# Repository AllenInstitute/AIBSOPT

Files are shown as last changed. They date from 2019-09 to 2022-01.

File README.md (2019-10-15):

Optical projection tomography microscope for isotropic imaging of intact, cleared mouse brains.  Designed specifically for imaging probe tracks in mouse brains following Neuropixels recordings. 

Instrument described is very low cost (~$6k US), straightforward to assemble out of mostly commercially-available parts, and with little need for maintenance or alignment.

Images acquired by this instrument can be reconstructed using free NRecon software (SkyScan via Bruker) and aligned to Allen Institute for Brain Science Common Coordinate Framework. Detecting probe tracks in these images allows registration of multiple experiments into a common spatial framework for comparing results across experiments. 

Repository contents:
- 412792_fluorSubset.gif - stack of reconstructed images from portion of mouse brain showing multiple Neuropixels tracks
- .\InstrumentBuild : 
    - Parts list
    - .\CAD : CAD design for instrument
    - .\EAGLE : Schematic for motor control shield.
    
- .\Software : 
    - .\InstrumentSoftware :  
      - .\Arduino\diyOPT : Sketch for motor driver board
      - .\MicroManager : Config file and acquisition script for data acquisition
    - .\DataProcessing : 
        - Python code to generate files + folders for NRecon reconstructions
        - Python utilities to aid in alignment using images of a test object on instrument
    - .\Analysis : Code for post-reconstruction volume registration and probe tracing 
- .\Protocols : 
  - Standard operating protocol for sample mounting, instrument operation, and reconstruction with NRecon.

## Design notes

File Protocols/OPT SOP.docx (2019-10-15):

OPT SOP

Technical Authors & Contributors

Department | Name
Imaging | Rusty Nicovich, Mike Taormina , Nhan-Kiet Ngo
Structured Science

Date of SOP Creation (Version 1.0): 7/1/2019

Periodic Review

[ ] Biannual [ ] Annual [ ] Biennial [x] None Last Review: 10/14/2019

Departmental Sign-Off

Department | Approval Required | SOP Reviewed | Name
Imaging | [ ] | [ ] | Rusty Nicovich
Engineering | [ ] | [ ]
Health and Safety | [ ] | [ ]
Scientific Lead | [ ] | [ ]

1.0 Scope: This protocol describes the imaging and image processing of OPT.
2.0 Materials:
  2.1. Specially cleared mouse brain specimens.
  2.2. Loctite 404 superglue.
  2.3. Stainless steel circular mounting disks.
  2.4. Kimwipes.
  2.5. Tweezers.
  2.6. Solid waste bag.
  2.7. Dibenzyl ether.
  2.8. Razor blade.
  2.9. 100% ethanol.
3.0 Equipment:
  3.1. OPT imaging platform.
  3.2. Processing computer.
  3.3. External hard drive.
4.0 Safety:
  4.1. Nitrile Gloves.
  4.2. Lab coat.
5.0 Output: Fully imaged whole mouse brain in white and fluorescent lights.
6.0 Reference Documents:
  6.1. None.
7.0 Data Acquisition:
  7.1. Press the power button on the OPT machine.
  7.2. Press the On/Off button.
  7.3. Select Recall 2 to enable 18.0 V, < 1 A output on channel 2.
  7.4. Open Micro-Manager 2.0 on the computer and select the default options. Click Ok. See 7.4.1.

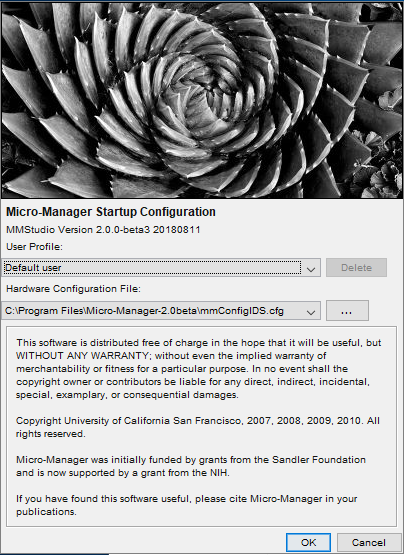
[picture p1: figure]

  7.5. Go to Tools → Script Panel → optacp.bsh.
    7.5.1. Create a storage folder in the following directory: D:\diyOPT\ and name the new folder using the following convention: xxxxyyzz where xxxx is the 4-digit year, yy is the 2-digit month, and zz is the 2-digit day.
    7.5.2. In optacp.bsh, baseFile = "" is the 6-digit specimen ID. Rename rootDirName = "D:/diyOPT/xxxxyyzz" to match the new folder just created. Then click "save". See 7.5.3 for example.

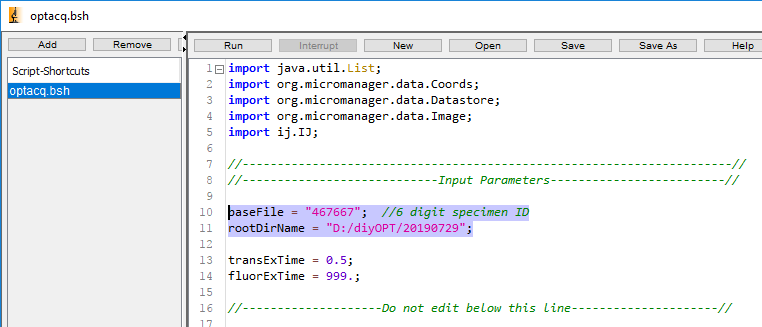
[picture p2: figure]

  7.6. Select a specimen to be imaged.
  7.7. Use a pair of tweezers to take the specimen out of its storage vial.
  7.8. Gently dab dry the specimen with Kimwipes.
  7.9. One small drop of Loctite 404 in the center of the mounting disk.
  7.10. Glue the cerebellum end of the specimen on to the disk. Wait at least one minute before using the tweezers to gently tap the specimen to make sure it's well glued.
  7.11. Mount the disk to the OPT imaging assembly.
  7.12. Center the disk and brain on the assembly. Tip: spin specimen with motor advance button on controller. At same time, use rounded object such as screwdriver handle to gently push disk to center brain on motor axis.
  7.13. Fill the imaging chamber with dibenzyl ether.
  7.14. Place the filled imaging chamber in the imaging area.
  7.15. Gently mount the imaging assembly into four post holders surrounding the filled imaging chamber. Make sure the amount of dibenzyl ether in chamber covers at least 1/3 of the specimen disk height but not completely submerge the disk. If there's any trapped air bubbles under the specimen disk, spin the mounting disk several times to get rid of them.
  7.16. Micro Manager control panel.

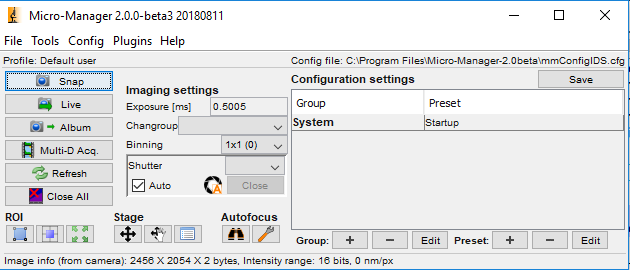
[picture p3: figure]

    7.16.2. In the Micro Manager control panel, click on Live. Turn the white light slide switch from TRIG to CW mode. White LED should now illuminate sample. In live view, determine the following:
      7.16.2.1. To determine the accurate exposure, adjust the light intensity (using LED controller knob) or exposure time (in MicroManager window) so that saturated hot spots just disappear and you have an even illuminating background without saturation. Using the limit-highlighting colormap is helpful here. See example of correct illumination in 7.15.2.2.

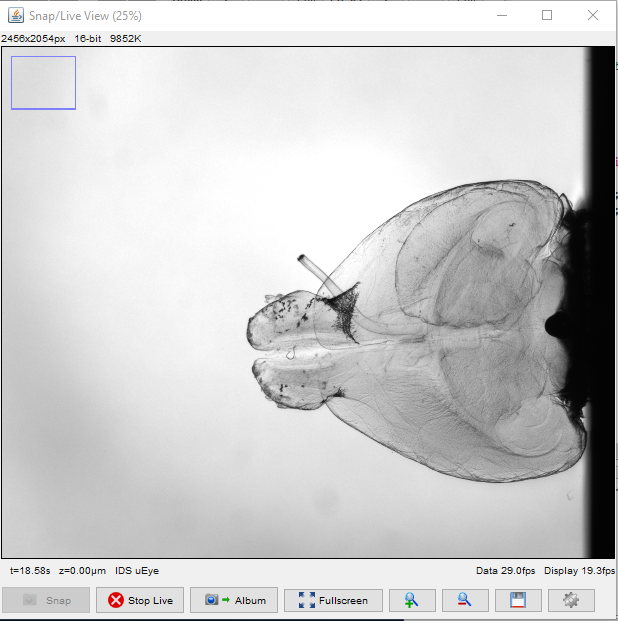
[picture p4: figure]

      7.16.2.3. The brain is well within the imaging area.
      7.16.2.4. Specimen is in focus.
      7.16.2.5. Use the stage micrometers to make any necessary adjustments to position and focus.
    7.16.3. Turn off live view (click ‘Stop Live’ in Micro Manager) and set white light controller to ‘TRIG’ position.
  7.17. Cover up the entire imaging platform with its box.
  7.18. After entering the 6-digit specimen ID in the optacq.bsh, click "Save" then "Run" in the script panel.
  7.19. The imaging process takes about six minutes to complete.
  7.20. Gently remove the imaging assembly from posts.
  7.21. Remove the mounting disk from the mechanism.
  7.22. Use razor blade safely and gently remove the brain from the disk.
  7.23. Use tweezers to place the specimen back into its original storage vial.
  7.24. Anything that comes directly in contact with dibenzyl ether needs to be throroughly cleaned by 100% ethanol. Solid waste goes into its storage bag.
  7.25. Use razor blade to remove any glue residue on the mounting disk.
  7.26. Store the specimens appropriately.
  7.27. Transfer the newly collected data to the processing station via the external hard drive.
8.0 Data Processing.
  8.1. On the processing computer, in D:\Data\diyOPT\ create a folder with exact same name as the data folder want to transfer over. This is the data storage folder.
  8.2. Open Spyder and script stackToPlanes.py. Set script variables to:
    8.2.1. inputFolder: Directory path of data folder from the external hard drive.
    8.2.2. outputFolder: Directory path of data folder created in 8.1. See example in 8.2.3

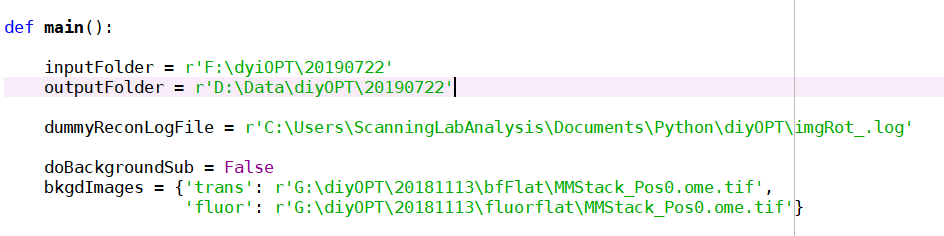
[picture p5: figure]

    8.2.4. Run stackToPlanes.py script in Python. Images and folders should be created in destination outputFolder designated in steps 8.1 and 8.2.3.
  8.3. Open Nrecon, then open specimen folder to be processed.
  8.4. Open the translucent (trans) folder first. Select the first image.
  8.5. Start tab:
    8.5.1. Position the green horizontal line at the specimen's widest section.
    8.5.2. Position the top horizontal line to be above speciemen's highest point.
    8.5.3. The value for bottom horizontal line is the amount necessary to exclude the black bar. See 8.5.3.1 for example:

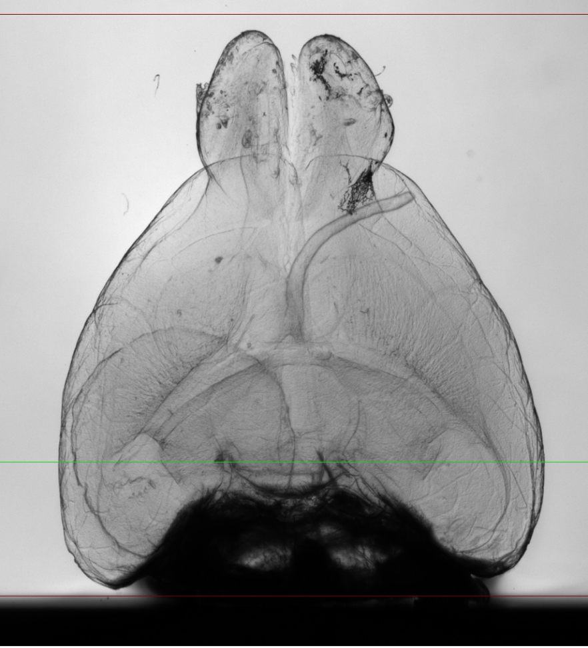
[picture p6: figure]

Black bar

    8.5.4. Record the values for Top and Bottom of range.
    8.5.5. Example:

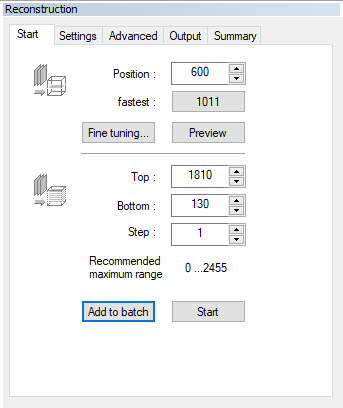
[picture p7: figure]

  8.6. Settings tab.
    8.6.1. Set Smoothing value to 3.
    8.6.2. Set Misalignment compensation value. This value is usually but not always, between -25 and -35. If the range is out side of -25 and -35, change the value until images align directly on top of each other. There should be no double images.
    8.6.3. Example:

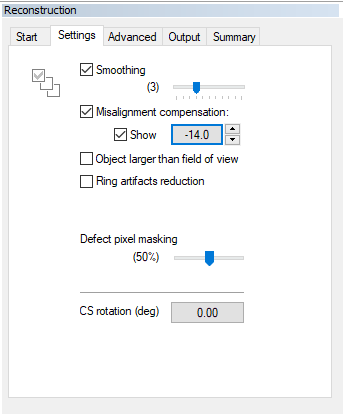
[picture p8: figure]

  8.7. Output tab.
    8.7.1. Uncheck Scales ON box.
    8.7.2. Destination: Browse and open the recon folder in the trans folder.
    8.7.3. File format: TIF(16).
    8.7.4. Example:

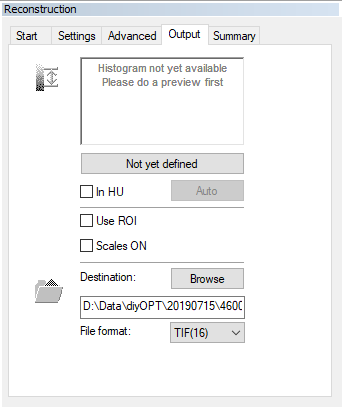
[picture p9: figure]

  8.8. Back to Start tab → Fine tuning → Number of trials = 10 trials → Start → Ok.
    8.8.1. Example:

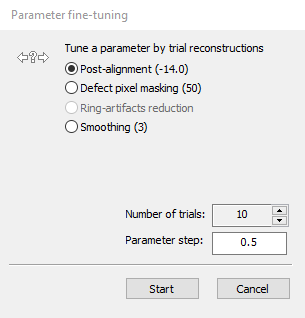
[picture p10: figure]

  8.9. After the trials are completed, in the Output tab, select the right vertical line and set all the way to the right of the histogram. Select the left vertical line and place it to the left of the base of the peak.
    8.9.1. Example:

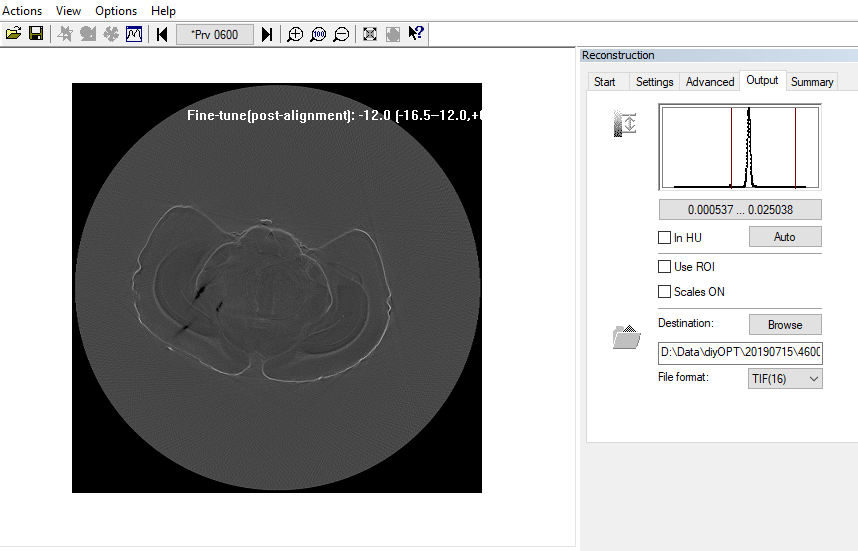
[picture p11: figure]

  8.10. Click on either the foward or backward arrow to determine the best-aligned image.
    8.10.1. Perfect alignment: top, bottom, left, and right all align with each other.

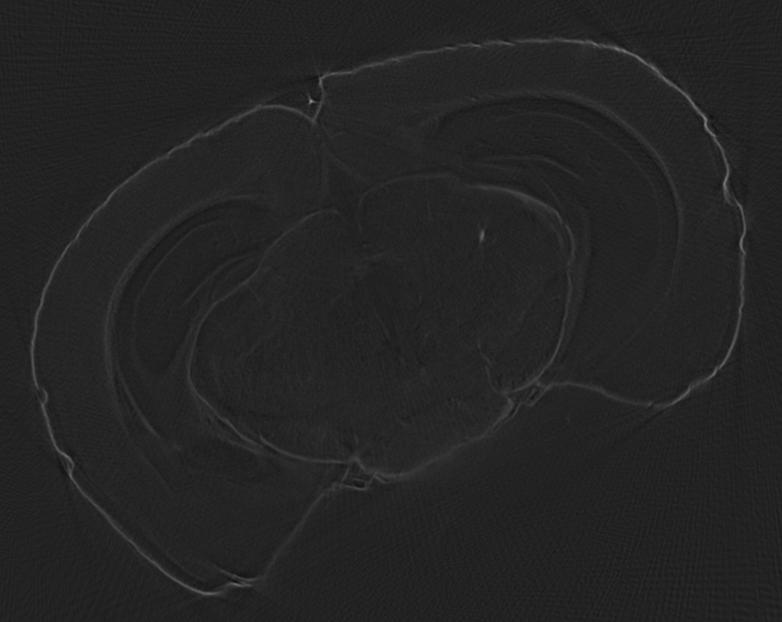
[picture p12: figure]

    8.10.2. Bad alignment: double image.

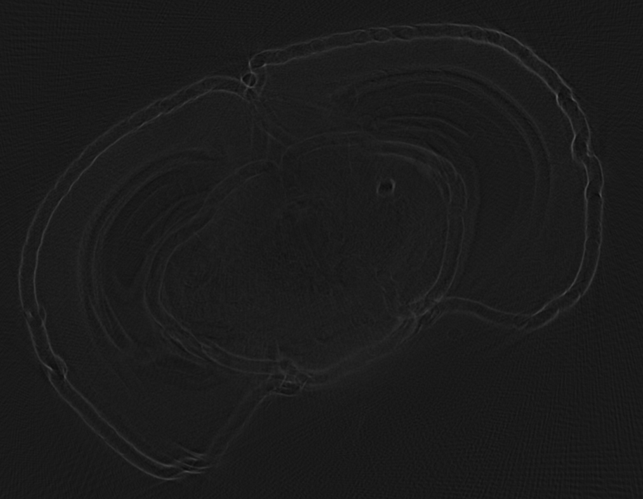
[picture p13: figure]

    8.10.3. Very poor alignment: no two parts can perfectly align with each other.

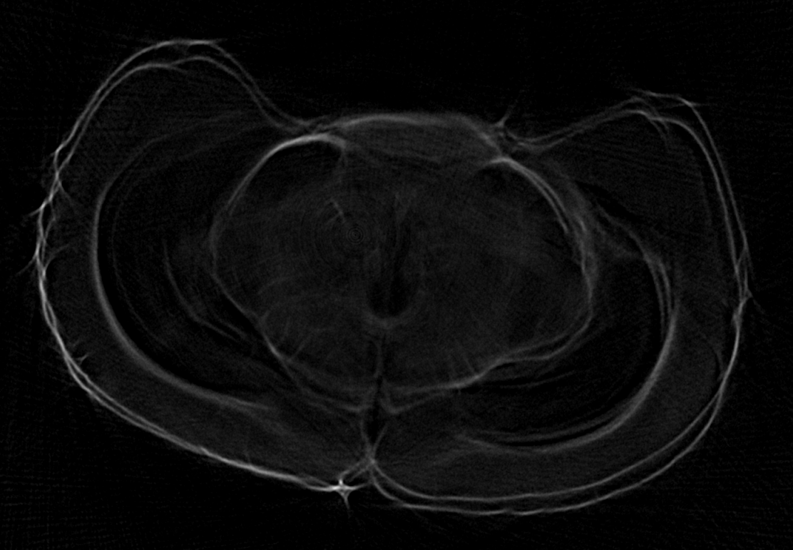
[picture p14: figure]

  8.11. Start tab → Add to batch.
  8.12. Open the fluorescent (fluor) folder of the same specimen. Select the first image, and repeat steps 8.5 – 8.9. For steps 8.5.1 – 8.5.4, enter the values for Top, Bottom, and Misalignment compensation you got from the transmitted channel. Make sure the destination is the recon folder inside the fluor folder.
  8.13. After completing all above steps for all specimens needed to be processed, go through the pending list to make sure all are 16-bit TIF.
  8.14. Start batch and let the processing runs overnight.
  8.15. Upon completion the next day, transfer data to the project's directory over the network.
9.0 Takedown:
  9.1. Clean work area. All items exposed to dibenzyl ether must be cleaned thoroughly by 100% ethanol.
  9.2. Store solid waste in its storage bag.
  9.3. Return the dibenzyl ether tub to the hood. Place a cover on it.
10.0 Precautionary: Dibenzyl ether is mildly toxic and corrosive. It's both storage and imaging medium. Wear PPE and exercise appropriate precautions.

Page 2 of 12 OPT SOP

Page 2 of 5 OPT SOP

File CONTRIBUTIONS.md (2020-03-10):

Allen Institute Contribution Agreement
This document describes the terms under which you may make “Contributions” — which may include without limitation, software additions, revisions, bug fixes, configuration changes, documentation, or any other materials — to any of the projects owned or managed by the Allen Institute. If you have questions about these terms, please contact us at terms@alleninstitute.org.  
You certify that:
•	Your Contributions are either:
1.	Created in whole or in part by you and you have the right to submit them under the designated license (described below); or
2.	Based upon previous work that, to the best of your knowledge, is covered under an appropriate open source license and you have the right under that license to submit that work with modifications, whether created in whole or in part by you, under the designated license; or
3.	Provided directly to you by some other person who certified (1) or (2) and you have not modified them.
•	You are granting your Contributions to the Allen Institute under the terms of the 2-Clause BSD license (the “designated license”).
•	You understand and agree that the Allen Institute projects and your Contributions are public and that a record of the Contributions (including all metadata and personal information you submit with them) is maintained indefinitely and may be redistributed consistent with the Allen Institute’s mission and the 2-Clause BSD license.

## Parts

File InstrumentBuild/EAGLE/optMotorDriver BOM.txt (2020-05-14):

Bill of Materials:

Motor Driver

Qty 1	-	PCB - https://oshpark.com/shared_projects/akx3myRT
Qty 1	-	BigEasyDriverBoard; Sparkfun ROB-12859
Qty 48	-	Male header strip; Adafruit 392 or equivalent
Qty 1	-	Wurth Electronik 62400821722 - 2 x 4 pin connector
Qty 8	-	Adafruit 1 x 2 @ 3.5 mm screw terminal 
Qty 7	-	10kΩ resistors, 1206 package
Qty 1	-	5.2mm SMD tactile switch
Qty 1	-	2.1mm x 5.5mm THM DC jack with internal switch. Digikey part #PJ-102A, 4UCON part #05537   

Button board

Qty 1	-	PCB	-	https://oshpark.com/shared_projects/rrk3NWli
Qty 2	-	Sparkfun COM-09190 - 12 mm pushbutton switch
Qty 5	-	Nidek Copal Electronics ATE1E-2M3-10-Z - toggle switch
Qty 1	-	Wurth Electronik 62400821722 - 2 x 4 pin connector

Connector cable

Qty 2	-	Wurth Electronik 624008213322 - 2 x 4 pin terminal housing
Qty 16	-	Molex 0008700058 crimp socket, 22-28 AWG
Qty 1	-	8 connector, 26 AWG cable, 1m; Tensility International Corp 30-01319

------------------------------------------------------------------------------------

Build Notes:

Stepper motor mounts to A and B coil ports. Connect light sources to 'ChanX' output terminal block.  
Thorlabs LED T cubes connect through BNC pigtail cable. 
Connecting camera to trigger terminal is optional.  
Power through wall wart supply with 5.5 mm x 2.1 mm connector, 12v, 0.5 A output.

Button board lets you switch on/off channels, move motor outside the enclosure.

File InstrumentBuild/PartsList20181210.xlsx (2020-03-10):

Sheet: DemoSystem
Sub-asssembly | Component | Vendor | Part Number | Qty | Price per | Total price | Notes
Imaging | Imaging lens | Edmund Optics | 62-932 | 1 | $1495.00 | $1495.00
 | Thread adapter | Edmund Optics | 59-450 | 1 | $25.00 | $25.00
 | Emission filter | Edmund Optics | 64-635 | 1 | $195.00 | $195.00 | 50 mm; 575 LP
 | Imaging lens mount | Edmund Optics | 63-442 | 1 | $295.00 | $295.00
 | Mount risers | Thorlabs | RS4M | 3 | $7.67 | $23.01 | Under lens mount
 | Filter holder | Edmund Optics | 83-340 | 1 | $50.00 | $50.00
 | Camera | 1st Vision | UI-3280CP | 1 | $1030.00 | $1030.00 | 2/3" format; 3.45 µm pixels
Fluor LED | Excitation LED | Thorlabs | M530L3 | 1 | $223.00 | $223.00
 | Collimation lens | Thorlabs | ACL2520U-DG6-A | 1 | $29.94 | $29.94
 | Excitation filter | Chroma | ET535/70m-2P | 1 | $375.00 | $375.00
 | LED driver | Thorlabs | LEDD1B | 1 | $314.13 | $314.13
 | LED mount | Thorlabs | SM1RC | 1 | $24.37 | $24.37
 | Power supply | Thorlabs | KPS101 (https://www.thorlabs.com/thorproduct.cfm?partnumber=KPS101) | 1 | $34.33 | $34.33
 | Lens tube | Thorlabs | SM1L05 | 2 | $12.59 | $25.18 | One upstream of adjustable tube; one w/ filter
 | Pedistal post | Thorlabs | RS1P | 1 | $23.64 | $23.64
 | Post clamp | Thorlabs | CF038-P5 | 0.2 | $40.19 | $8.04
 | Pedistal spacer | Thorlabs | RS3M | 1 | $7.67 | $7.67
 | Lens tube, adjustable | Thorlabs | SM1V05 | 1 | $30.25 | $30.25
Trans LED | Transmission LED | Thorlabs | MNWHL4 | 1 | $154.50 | $154.50
 | Lens tube, 0.3" | Thorlabs | SM1L03 | 1 | $12.16 | $12.16
 | LED collimator | Thorlabs | SM2F32-A | 1 | $277.36 | $277.36
 | Diffuser | Thorlabs | DG20-600 | 1 | $18.07 | $18.07
 | LED mount | Thorlabs | SM1RC | 1 | $24.37 | $24.37
 | Post clamp | Thorlabs | CF038-P5 | 0.2 | $40.19 | $8.04
 | Pedistal post | Thorlabs | RS1P | 1 | $23.64 | $23.64
 | Pedistal spacer | Thorlabs | RS3M | 1 | $7.67 | $7.67
 | LED driver | Thorlabs | LEDD1B | 1 | $314.13 | $314.13
 | Power Supply | Thorlabs | KPS101 (https://www.thorlabs.com/thorproduct.cfm?partnumber=KPS101) | 1 | $34.33 | $34.33
XY Stage assembly | XY Stage | Thorlabs | XYT1 | 1 | $552.62 | $552.62
 | 1/2" posts | Thorlabs | TR2 | 4 | $5.19 | $20.76 | 2" long
 | Post holders | Thorlabs | PH2 | 4 | $7.70 | $30.80 | 2" long
 | Post bases | Thorlabs | BE1 | 4 | $9.77 | $39.08
 | Post clamps | Thorlabs | CF038-P5 | 1.6 | $40.19 | $64.30 | May need CF125; 4 for stage and 4 for breadboard
 | Post collars | McMaster | 6157K14 | 4 | $2.94 | $11.76
 | Breadboard | Thorlabs | MB624 | 1 | $157.59 | $157.59
 | Breadboard feet | Thorlabs | RS1P | 4 | $23.64 | $94.56
Motor and sample mount | Rotating bearing | McMaster | 6383K23 | 1 | $5.52 | $5.52
 | Retaining rings | Thorlabs | SM1RR | 2 | $4.50 | $9.00
 | Shaft | -- | -- | 1 |  |  | Made in-house
 | Magnetic chuck | Thorlabs | BE1R | 1 | $17.23 | $17.23
 | Brain pucks | -- | -- | 1 |  |  | Made in-house; Make additional for throughput
 | Motor | -- | -- | 1 |  |  | 0.9 degree; NEMA 17
 | Motor mount | -- | -- | 1 |  |  | Made in-house
 | Motor lift mounts | Thorlabs | RS1P | 4 | $23.64 | $94.56
 | Motor lift mount clamps | Thorlabs | CF038-P5 | 0.8 | $40.19 | $32.15
Control electronics | Control board | SparkFun | DEV-11021 | 1 | $22.95 | $22.95
 | Motor driver | SparkFun | ROB-12859 | 1 | $19.95 | $19.95 | On in-house shield
 | USB-A to USB-B cable | Amazon | B00NH11KIK | 1 | $5.10 | $5.10 | 6' long
 | BNC pigtail cable | -- | -- | 2 |  |  | Made in-house
 | Power supply | -- | -- | 1 |  |  | Must supply 18V @ 1 A; 5.5 mm x 2.1 mm connector with optMotorDriver
 | Board mount | -- | -- | 1 |  |  | In-house design; 3D printed
 | Motor driver Arduino shield | -- | -- | 1 |  |  | In-house design; See ./AIBSopt/EAGLE/
PC | Control PC | -- | -- | 1 |  |  | 1 x USB 2.0+; 1 x USB 3.0; 3+ TB HDD; Win 10 OS
 |  |  |  | Total | $6260.76

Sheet: LaserLaunch
Sub-asssembly | Component | Vendor | Part Number | Qty | Price per | Total price | Notes

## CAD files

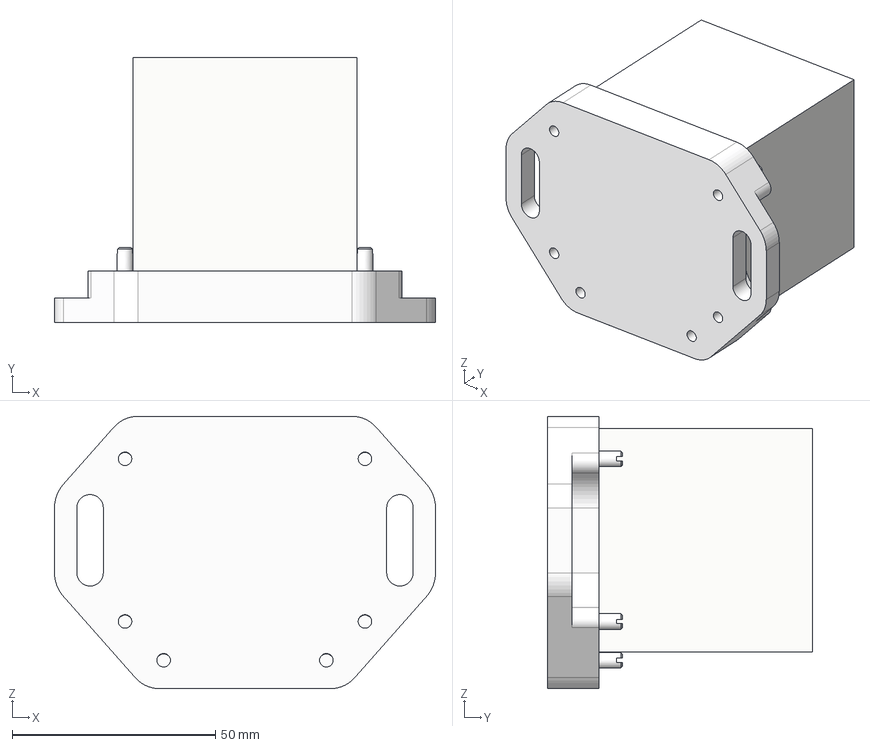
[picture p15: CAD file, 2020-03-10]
InstrumentBuild/CAD/toMachine/CuvetteStandAssembly.step
93.7 x 65.2 x 67.0 mm
50mmCuvette
McMaster 97493a114 x 6

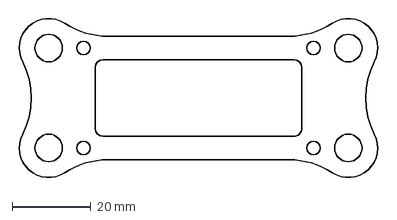
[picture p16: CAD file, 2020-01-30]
InstrumentBuild/CAD/DriverBoard/OPTButtonBoardTableMount.dxf
92.7 x 41.7 mm

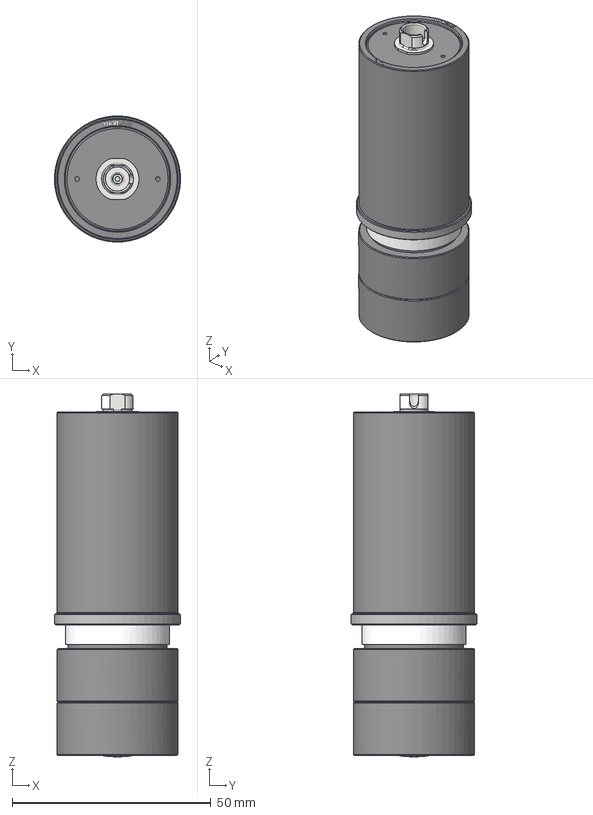
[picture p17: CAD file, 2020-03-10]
InstrumentBuild/CAD/LaserLaunch/hexLaserCoupler.step
31.7 x 31.7 x 91.3 mm
94355A140 x 6
HexLightPipeToSM1Adapter
SM1L05-Solidworks
SM1V05-Solidworks v1
SM1RR x 2
AC254-035-A-Solidworks
SM1FC-Solidworks
step_65830
SM1M20-Solidworks v1

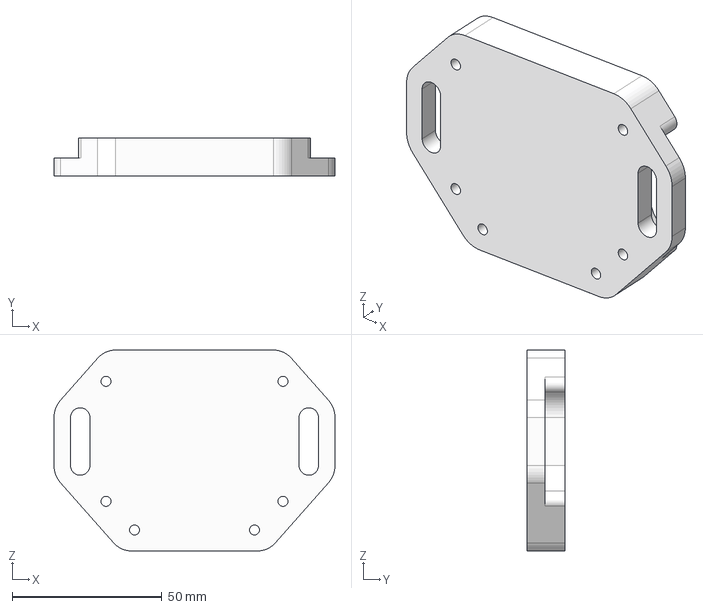
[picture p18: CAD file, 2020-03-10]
InstrumentBuild/CAD/toMachine/OPTCuvetteBase.step
93.7 x 12.7 x 67.0 mm

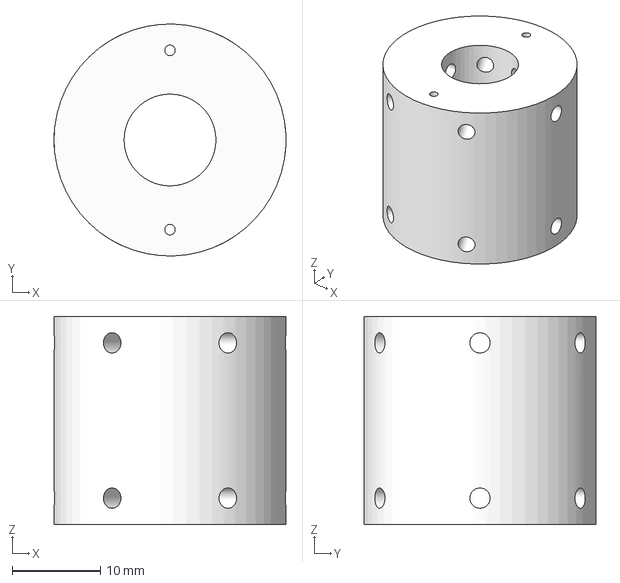
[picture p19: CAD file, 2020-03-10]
InstrumentBuild/CAD/toMachine/HexLightPipeToSM1Adapter.step
26.3 x 26.3 x 23.6 mm

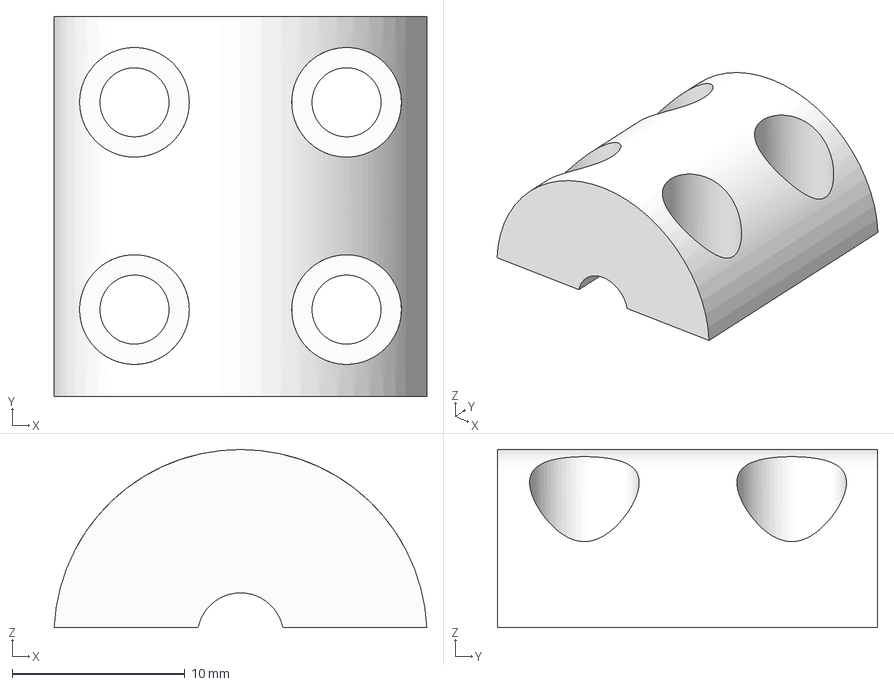
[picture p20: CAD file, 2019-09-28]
InstrumentBuild/CAD/toMachine/BearingShaftClamp.step
21.6 x 22.0 x 10.3 mm

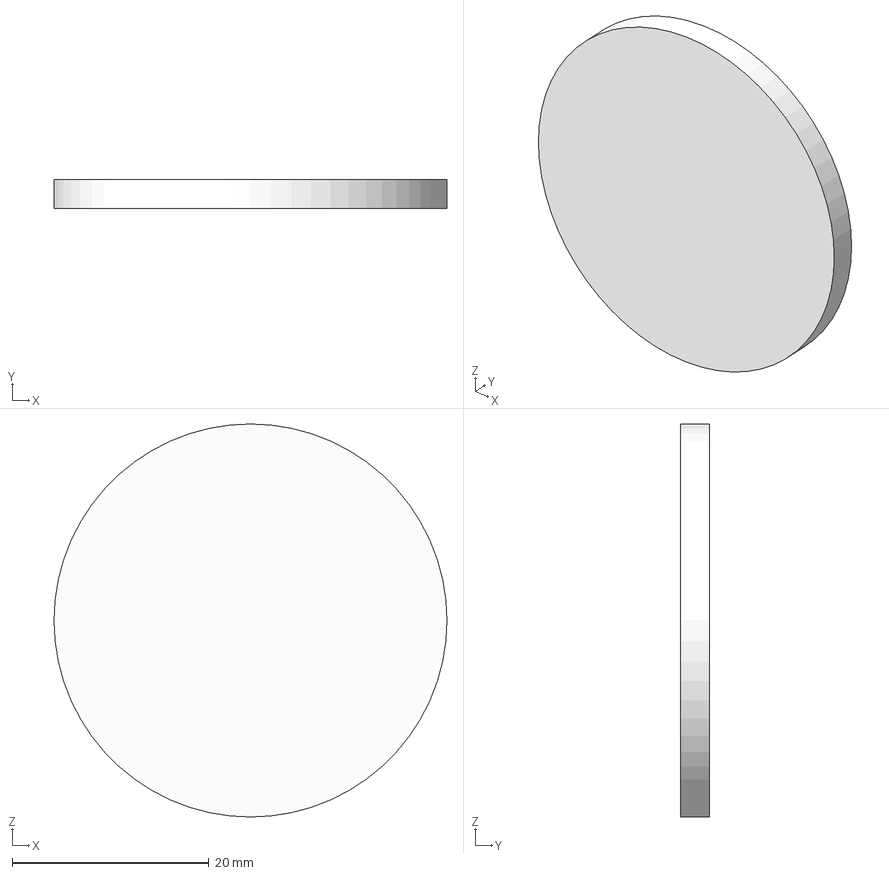
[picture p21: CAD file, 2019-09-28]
InstrumentBuild/CAD/toMachine/sampleHolderPuck.step
40.0 x 3.00 x 40.0 mm

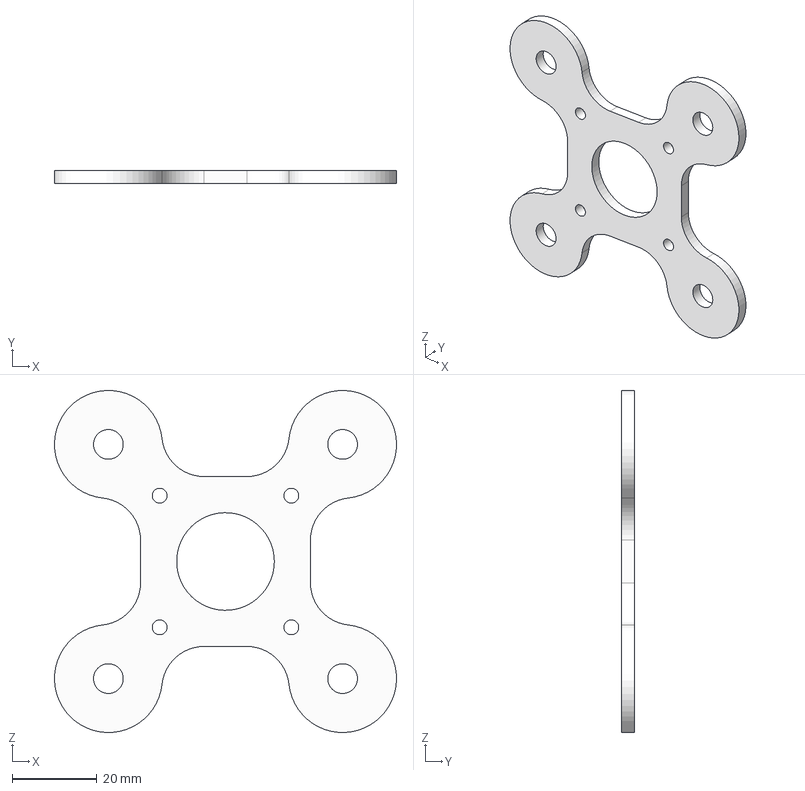
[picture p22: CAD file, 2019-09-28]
InstrumentBuild/CAD/toMachine/Nema17OPTmotorMountv2 v2.step
80.5 x 3.18 x 80.5 mm

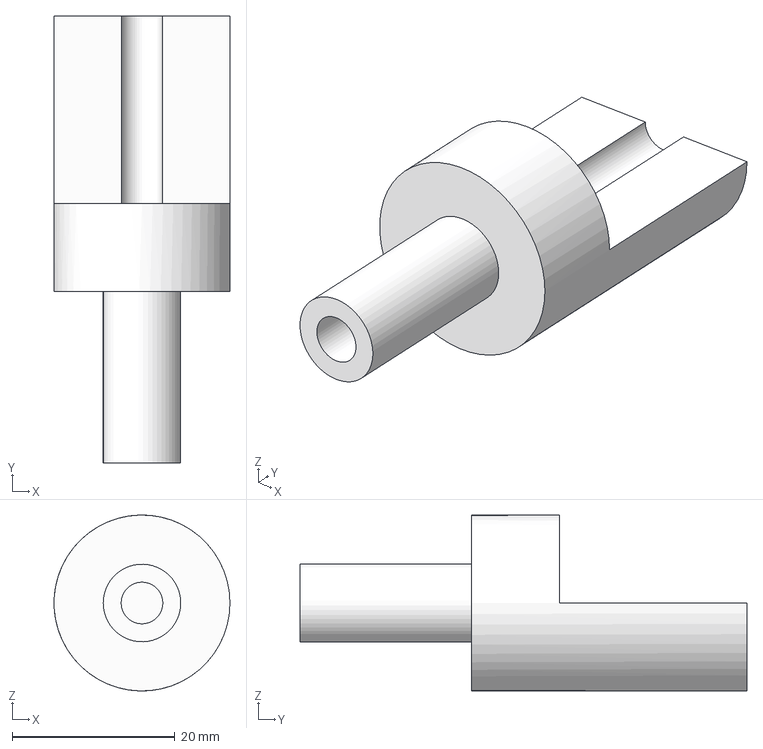
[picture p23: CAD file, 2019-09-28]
InstrumentBuild/CAD/toMachine/BearingShaft.step
21.6 x 54.9 x 21.6 mm

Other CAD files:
InstrumentBuild/CAD/toMachine/HexLightPipeToSM1Adapter.stl

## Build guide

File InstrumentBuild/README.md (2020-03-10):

Components and assembly for AIBSOPT

# CAD
	Includes STEP file of instrument assembly with all physical components and instrument rendering.  
	
	.\CAD\toMachine includes individual STEP files and drawings of parts to machine:
		- Extended motor shaft (BearingShaft.step, BearingShaftClamp.step, diyOPTShaftExplode Drawing v0.pdf). Make 1 assembly from aluminum. 
		- Motor mount (Nema17OPTmotorMountv2 v2.step and .pdf). Make 1 from aluminum. 
		- Sample holder puck (sampleHolderPuck.pdf and .step).  Make 1-4 from *magnetic* stainless steel.
		- Specimen chamber (specimenChamberBuildNotes.txt):
			DIY - slideSpecimenChamber drawing v1.pdf
			----OR----
			Purchase Hellma 50 mm large cuvette (Sigma-Aldrich part Z805750), machine OPTCuvetteBase.step, assemble CuvetteStandAssembly.step

	.\CAD\DriverBoard
		- Files to laser cut mount for optMotorButtonBoard to Imperial optical table.  Cut from acrylic and use standard PCB stand-offs to mount PCB.
		
	.\CAD\laserLaunch
		- Assemblies and build details on adding laser illumination to OPT.  Includes laser combiner + launch w/ speckle reducer and fiber coupling, enclosure, and laser illuminator.

# PCB Files

	.\EAGLE : Schematic for Arduino motor shield and remote button board for instrument control.
		- optMotorDriver BOM.txt includes parts required for assembly and links to order PCB
		- Can upload .brd files to favorite PCB fab service to order
		- Mount to optical table with .\CAD\DriverBoard part

# Notes on assembly and alignment:

Final resolution of instrument is primarily dependent on alignment of all images in the rotation stack. The rotation axis *MUST* be aligned to camera optical axis, with no roll or pitch.  Yaw is actually well-tolerated.  Roll (camera rotating around optical axis/rotational axis tilted left or right) and pitch (aka nod, rotation axis tilted towards or away from camera) manifest as misalignment in the collected image stack and blur or double-image artifacts in the reconstructions.  

Steps for aligning the roll and pitch axes follow those well-described in https://doi.org/10.1371/journal.pone.0073491.  An object, such as a small ball bearing or tip of a hypodermic needle mounted on the sample holder using glue and/or magnets, provides a good fiducial marker.  This item or a feature on it should be able to be localized in images to sub-pixel precision.  Tracking this feature through the stack should produce a straight line parallel to one axis of the camera.  Any tilt is evidence of roll; elliptical character evidence of pitch.  The .\Software\DataProcessing\assessTestObject.py script is helpful in this step.

Adjustments can be made through small movements of the XY stage and motor.  This assembly should rest equally on all four of the shaft collars on the 1/2" mounting posts.  Typically the screws in the post holders are left open so that the posts freely drop to the proper position.  Shims made from shim stock or a cleaned and dissected soda can make small adjustments to the stage tip or tilt for testing alignment.  If a good position is found, this can be set in place by tightening the post holder screws with the shims in place, removing the shims, then lowering the shaft collars hard against the post holders before tightening the collar screws.  Then when the stage is lifted out and returned, it should return to the same position defined by the shaft collars against the top of the post holders.

Additional care must be taken to have specimen remain within camera field of view while rotating and remain in focus.  Both are straightforward to deal with using the adjusters on the XY stage.  The depth of focus can be increased using the built-in aperture iris on the telecentric lens.  Best to have this be close to the full depth of the specimen without overly darkening the images.  In practice the lost sharpness in the images is negligable compared to the blur induced by mis-alignment.

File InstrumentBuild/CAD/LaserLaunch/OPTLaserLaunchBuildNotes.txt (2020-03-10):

Build notes for laser illumination on AIBS OPT.

Goal is to have a high-powered light source with narrow line widths for improved imaging performance over LED illumination.  Laser line widths make it easier to find appropriate optical filters for multi-colored imaging.  

For laser launch, requirement is for lasers in desired wavelengths combined into single multi-mode fiber with despeckler.  Implementation here is a simplified NicoLase 1200 design supporting two diode lasers (488 nm and 552 nm nominal wavelengths) with EvenField despeckler into Thorlabs square-core multimode fiber. Fiber choice is dictated by NA. The square-core Thorlabs fiber has an NA of 0.39; Thorlabs also sells a number of typical round-core fibers with same or higher NA for ~$50 less. Any should work but only the square-core fiber we had on hand was tested.   

Small footprint of the laser launch allows it to fit onto a 12" x 12" breadboard for easy deployment. Two lines is sufficient for desired experiments. Enclosure holds laser launch in compact box that is easy to fit on a shelf.  Drill some holes into top panel and you can use screws or zip ties to mount laser control remotes and motor driver board on exterior.  

Illuminator takes fiber output and generates homogeneous hexagon of light at the specimen plane. Using a fiber of lower NA could result in less even illumination out of the hexagonal light pipe. In that case a longer light pipe (eg the Edmund 50 mm 49-402 vs Edmund 25 mm 63-082 quoted here) may be adventageous. The illuminator assembly fits into lens tubes of similar dimension to Thorlabs LED, so swapping out illumination choices is straightforward.

Illuminator uses a single lens to project front hexagonal face of light pipe onto specimen. This means focusing and magnfication are coupled. For the #63-082 pipe, the front face is 4.0 mm across the flats.  The illuminator should sit near the OPT collection lens, but behind the front element of that component.  This is a minimum distance of ~170 mm from the specimen.  With a f = 35 mm lens, this would mean placing the lens (1 / 35 mm) = (1 / 170 mm) - (1 / x) ; x = 44 mm away from the light pipe output.  This yields a M = 170 / 44 = 3.8x magnification, for a spot 15.2 mm across the hexagonal flats.  If the distance was 190 mm, the spot would be 17.6 mm.  In most cases a smaller spot size is preferred to preserve illumination intensity over the specimen, so a shorter distance (or longer focal length lens) is preferred.
 
TTL outputs from laser head or remote can go directly into OPT Motor Board.  Home-made SMB pigtails were used on our implementation.  

Cost is mostly price of laser diodes ($~15k for models used here), with another $~3k in optics, filters, and machined parts to complete build. 

~~~~~~~~~~  Laser launch ~~~~~~~~~~  

Bill of Materials
To machine:
NicoLase 1200 heat sink block : https://github.com/PRNicovich/NicoLase/blob/master/Hardware/HeatSinkMount/NicoLase3200HeatSinkBlock.step
Evenfield motor block and arbor : https://github.com/AllenInstitute/EvenField/blob/master/Hardware/CAD/diffuserMotorAssembly.step

Thorlabs:
[NicoLase 1200]
MB1212
POLARIS-K1 x 2
RP05P x 2
PF10-01-P01 
CF125 x 2

[Evenfield coupler]
KB1C
PF10-01-P01 
CP02
SM1L10
S1TM09
C220TMD
CT1
CT102
SM05FC
ER6 x 2
ER3
CP02B
RS6M
RS3M
RS05P x 2
M102L05
CF125 x 2

Chroma:
ZT514rdc in 25 mm round, mounted 
nb - substitute with part appropriate for your lasers

Edmund
[Evenfield illuminator diffuser]
#47-989, mounting ring removed and center hole drilled.  See https://github.com/AllenInstitute/EvenField/blob/master/Hardware/CAD/diffuserMotorAssembly.step

Polou:
#3036, gear motor

Laser diodes:
Coherent OBIS 552 nm, 100 mW with remote
Vortran Stradus 488 nm, 150 mW with remote
Any NicoLase-compatible laser diode will work here if you want different wavelengths.

Optional:
Evenfield motor driver :
https://github.com/AllenInstitute/EvenField/tree/PCBAddition/Hardware/MotorDriverPCB

~~~~~~~~~~  Enclosure ~~~~~~~~~~ 

Assembly is in file ./AIBSOPT/InstrumentBuild/CAD/OPTLaserLaunch.step.

Bill of Materials
To machine:
Panels were made from 1/4" black foamcore (Thorlabs TB4).  
Top panel - 359 mm x 359 mm with 6.5 mm holes at 12.5 mm from corners, access slot for internal cables.
3 x Side panels - 324 mm x 150 mm with 12 mm x 15 mm knotchees in each corner. 
As per Side panel, but with 14 mm diameter holes for grommets for fiber, motor wires

80/20:
All 1" Series 10 T slot profile.  All taps 1/4"-20 and access holes 5.1 mm.
4 x 159 mm w/ end tapped, other end 2 x access holes at 12.7 mm
6 x 309 mm w/ both ends tapped
2 x 309 mm w/ both ends tapped, 2 x access holes on same face at 27 mm from either end
2 x 359 mm w/ 4 x access holes, 12.7 mm from both ends on both faces
Hardware:
20 x 3682 standard fastener
4 x 3313 roll-in T nut with set screw or similar
4 x 3382 slide-in T nut or similar

McMaster-Carr:
2 x 9307K131 grommets.  Split with knife to wrap around optical fiber.
4 x 9541K83 feet or similar

~~~~~~~~~~  Illuminator ~~~~~~~~~~ 

Bill of Materials:
To print/machine:
HexLightPipeToSM1Adapter - Print or machine from variety of materials - ./AIBSOPT/InstrumentBuild/CAD/toMachine/HexLightPipeToSM1Adapter.step or ./AIBSOPT/InstrumentBuild/CAD/toMachine/HexLightPipeToSM1Adapter.stl

Thorlabs:
SM1V05
SM1L05
2 x SM1RR
SM1FC
SM1M20
AC254-035-A (can substitute different focal length depending on application)

Edmund:
#63-082 light pipe

McMaster:
94355A217 or similar 4-40 set screws, 1/2" long recommended

~~~~~~~~~~  Emission filter ~~~~~~~~~~

Semrock FF01-512/630-50, mounted. Mount with existing adapter on front of collection lens.

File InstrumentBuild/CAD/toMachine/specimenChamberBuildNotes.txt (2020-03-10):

~~~~~~~~ DIY OPTION ~~~~~~~~ 

Specimen chamber for demo system built from 3 1/4" x 4" x 1.2 mm glass slides (Brain Research Laboratories part 3140).  These were cut to size w/ glass cutter and glued together with Dow Corning #732 clear silicone sealant.  That product from Dow has been robust to dibenzyl ether as immersion medium over months of use.  

Nominal dimensions of chamber are given in sliceSpecimenChamber drawing v1.pdf. As long as assembled chamber fits within space provided, can hold sufficient immersion medium to immerse specimen, and presents a flat face through transmission path to detection lens and to fluorescence excitation, dimensions can be altered significantly to suit.

~~~~~~~~ PURCHASE OPTION ~~~~~~~~ 

Commercial cuvette such as Hellma 50 mm large cell (Sigma-Aldrich Z805750) works well in this application.  Is easier to use and requires a smaller volume than the DIY cuvette above. Plus it doesn't have any chance of leaking!

On OPT, this cuvette sits on stand OPTCuvetteBase.step, machined from aluminum or other material impervious to immersion fluid.  This part has 6 places for 4 mm diameter locating pins (McMaster-Carr 97493A114), as shown in CuvetteStandAssembly.step.  In practice it is likely easier to use only 4, 2 to locate back edge of cuvette nearest to transmission path white LED, and 2 to locate one side of cuvette.  Then cuvette installation would involve pushing cuvette to be flush to these 4 pins.  Stand should be centered in light path and has some movement backwards + forwards towards collection lens to find best focus. Be sure to focus with target in immersion fluid in the cuvette!

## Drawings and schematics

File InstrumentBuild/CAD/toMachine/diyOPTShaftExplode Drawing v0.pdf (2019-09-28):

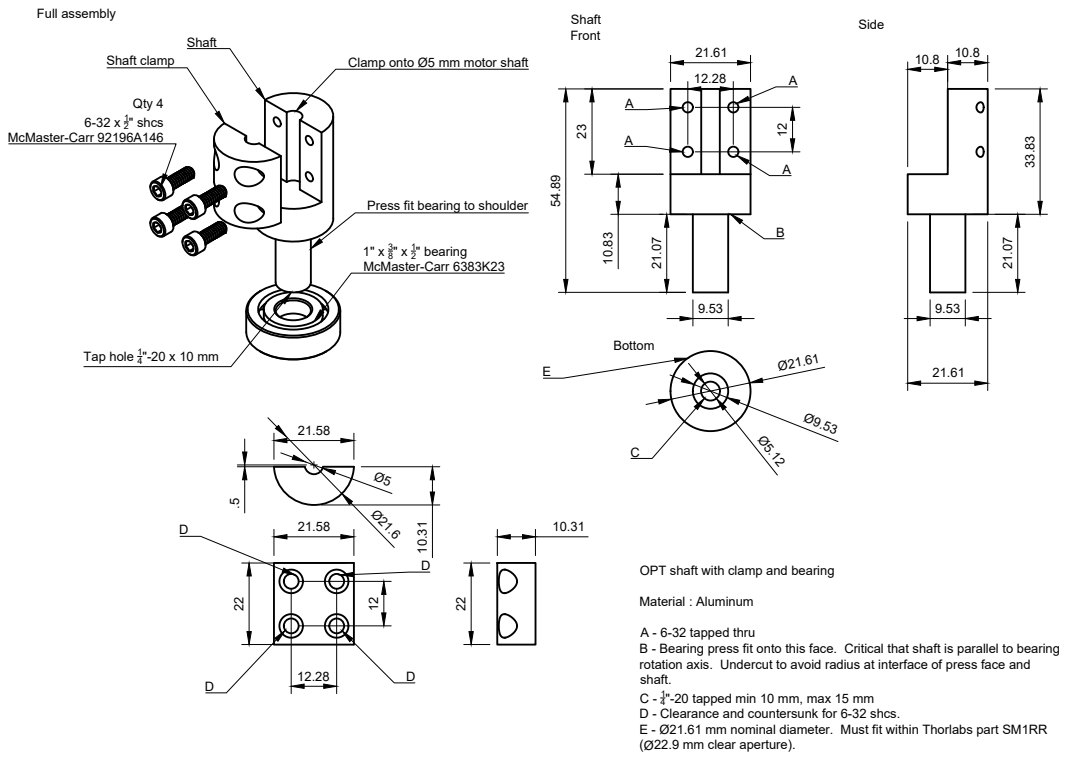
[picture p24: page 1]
Qty 4; 6-32 x 1 " shcs McMaster-Carr 92196A146; Shaft clamp; " x 1 " bearing McMaster-Carr 6383K23; Tap hole 1 "-20 x 10 mm; Material : Aluminum; Full assembly

Clamp onto Ø5 mm motor shaft

Press fit bearing to shoulder

OPT shaft with clamp and bearing

A - 6-32 tapped thru
B - Bearing press fit onto this face. Critical that shaft is parallel to bearing
rotation axis. Undercut to avoid radius at interface of press face and
shaft.
"-20 tapped min 10 mm, max 15 mm
D - Clearance and countersunk for 6-32 shcs.
E - Ø21.61 mm nominal diameter. Must fit within Thorlabs part SM1RR
(Ø22.9 mm clear aperture).

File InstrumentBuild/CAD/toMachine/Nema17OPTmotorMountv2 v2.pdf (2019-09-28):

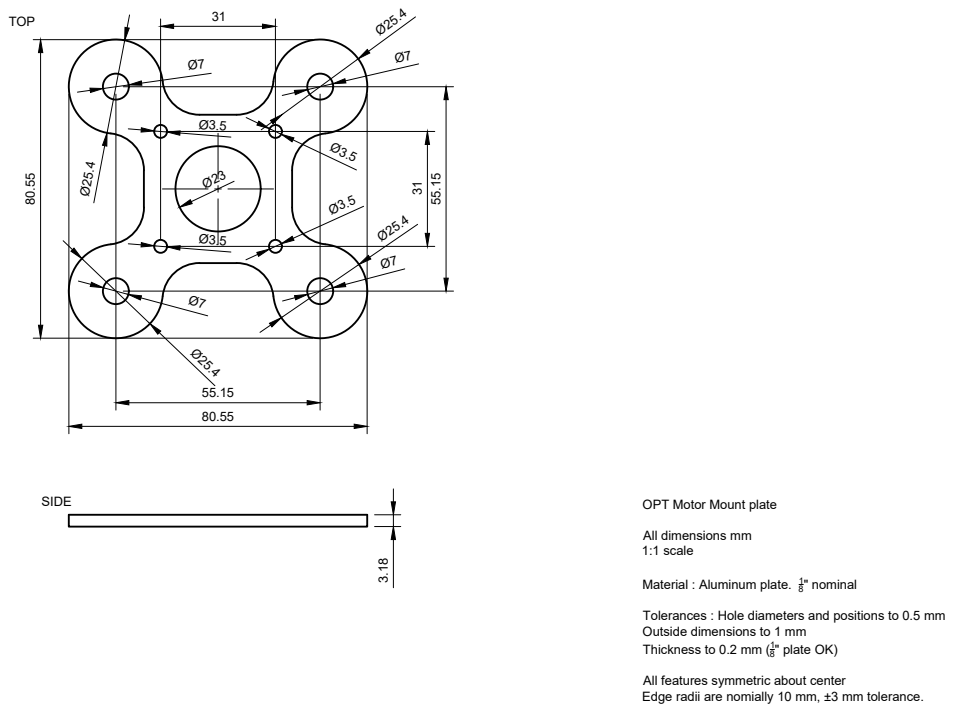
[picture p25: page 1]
" nominal; " plate OK)

OPT Motor Mount plate

All dimensions mm
1:1 scale

Material : Aluminum plate. 1

Tolerances : Hole diameters and positions to 0.5 mm
Outside dimensions to 1 mm
Thickness to 0.2 mm (1

All features symmetric about center
Edge radii are nomially 10 mm, ±3 mm tolerance.

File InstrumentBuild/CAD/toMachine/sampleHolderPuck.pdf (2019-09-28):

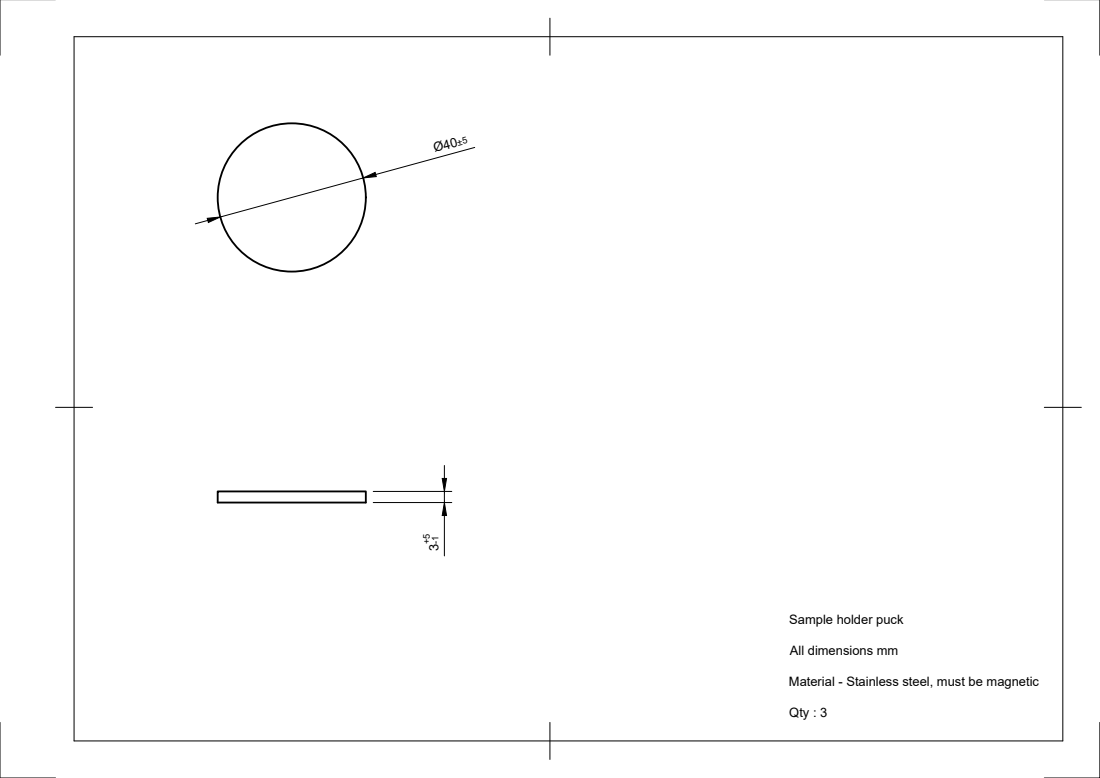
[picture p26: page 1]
Qty : 3

Sample holder puck

All dimensions mm

Material - Stainless steel, must be magnetic

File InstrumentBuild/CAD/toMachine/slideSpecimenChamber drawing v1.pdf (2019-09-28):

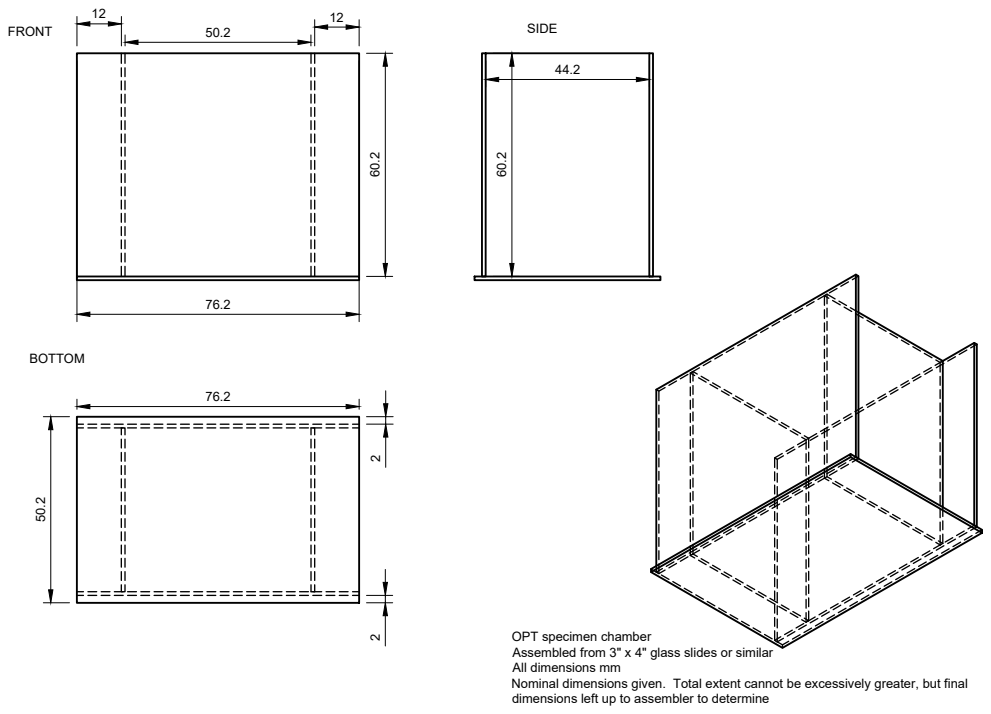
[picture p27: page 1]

OPT specimen chamber
Assembled from 3" x 4" glass slides or similar
All dimensions mm
Nominal dimensions given. Total extent cannot be excessively greater, but final
dimensions left up to assembler to determine

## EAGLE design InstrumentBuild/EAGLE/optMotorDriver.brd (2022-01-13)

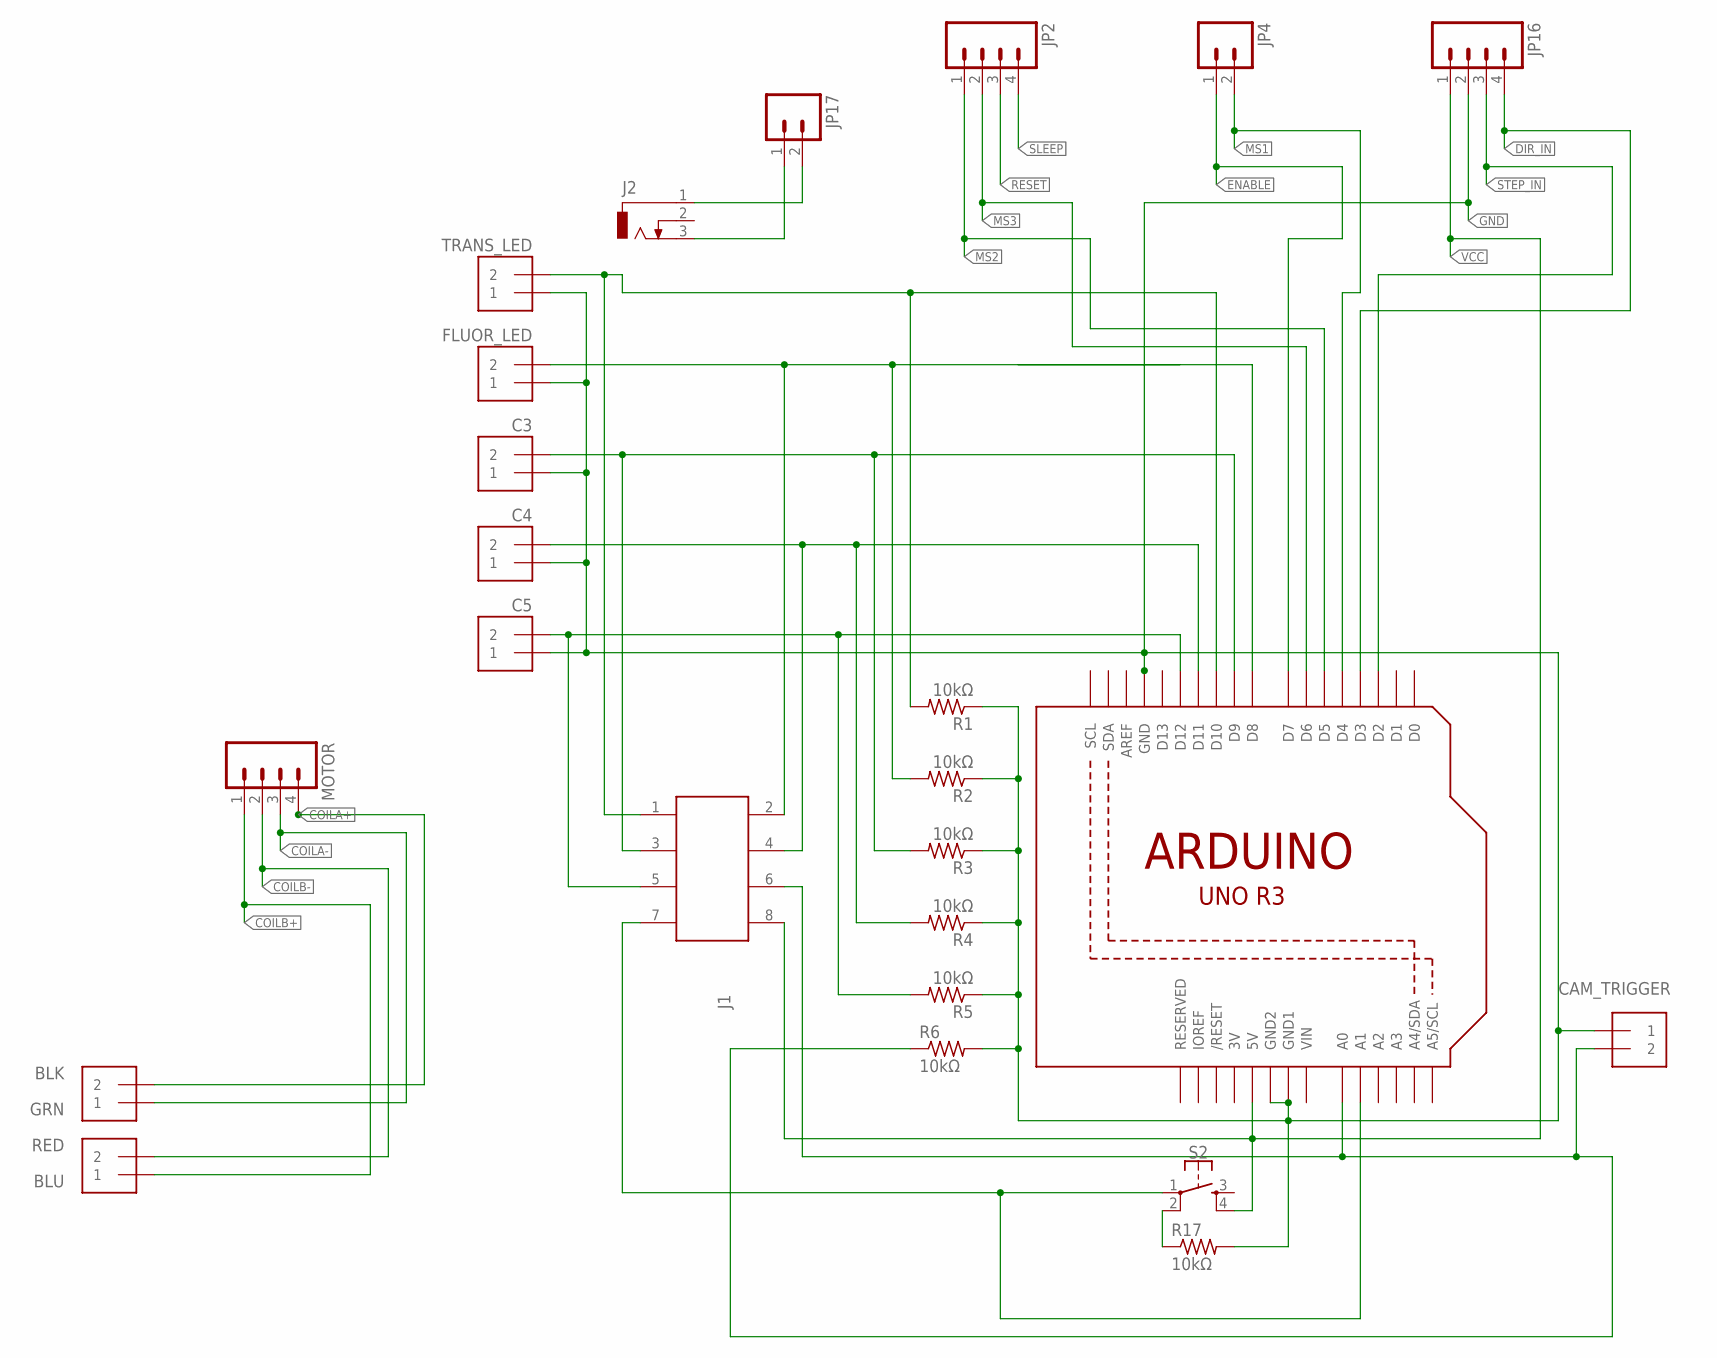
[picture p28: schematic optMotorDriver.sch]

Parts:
ACOIL: 1X2-3.5MM
BCOIL: 1X2-3.5MM
C1, C2, C3, C4, C5: 1X2-3.5MM
J1: 62400821722
J2: DCJ0303
JP2, JP16: M04PTH; 1X04
JP4, JP17: M02PTH; 1X02
MOTOR: M04PTH; 1X04
R1, R2, R3, R4, R5, R6, R17: 10kΩ; R1206
S2: MOMENTARY-SWITCH-SPST-2-SMD-5.2MM; TACTILE_SWITCH_SMD_5.2MM
TRIGGER: 1X2-3.5MM
U1: ARDUINOR3-DIMENSION; ARDUINOR3

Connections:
3V: U1.3V
COILA+: ACOIL.2, MOTOR.4
COILA-: ACOIL.1, MOTOR.3
COILB+: BCOIL.1, MOTOR.1
COILB-: BCOIL.2, MOTOR.2
DIR_IN: JP16.4, U1.D3
ENABLE: JP4.1, U1.D7
GND: C1.1, C2.1, C3.1, C4.1, C5.1, JP16.2, R1.1, R2.1, R3.1, R4.1, R5.1, R6.2, R17.2, TRIGGER.1, U1.GND, U1.GND1, U1.GND2
MS1: JP4.2, U1.D4
MS2: JP2.1, U1.D5
MS3: JP2.2, U1.D6
unnamed: J2.3, JP17.1
unnamed: C4.2, J1.4 (6), R4.2, U1.D11
unnamed: J2.1, JP17.2
unnamed: C3.2, J1.3 (5), R3.2, U1.D9
unnamed: C5.2, J1.5 (3), R5.2, U1.D12
unnamed: J1.7 (1), S2.1, U1.A1
unnamed: J1.6 (4), R6.1, TRIGGER.2, U1.A0
unnamed: C2.2, J1.2 (8), R2.2, U1.D8
unnamed: C1.2, J1.1 (7), R1.2, U1.D10
unnamed: R17.1, S2.2
RESET: JP2.3
SLEEP: JP2.4
STEP_IN: JP16.3, U1.D2
VCC: J1.8 (2), JP16.1, S2.4, U1.5V
VIN: U1.VIN

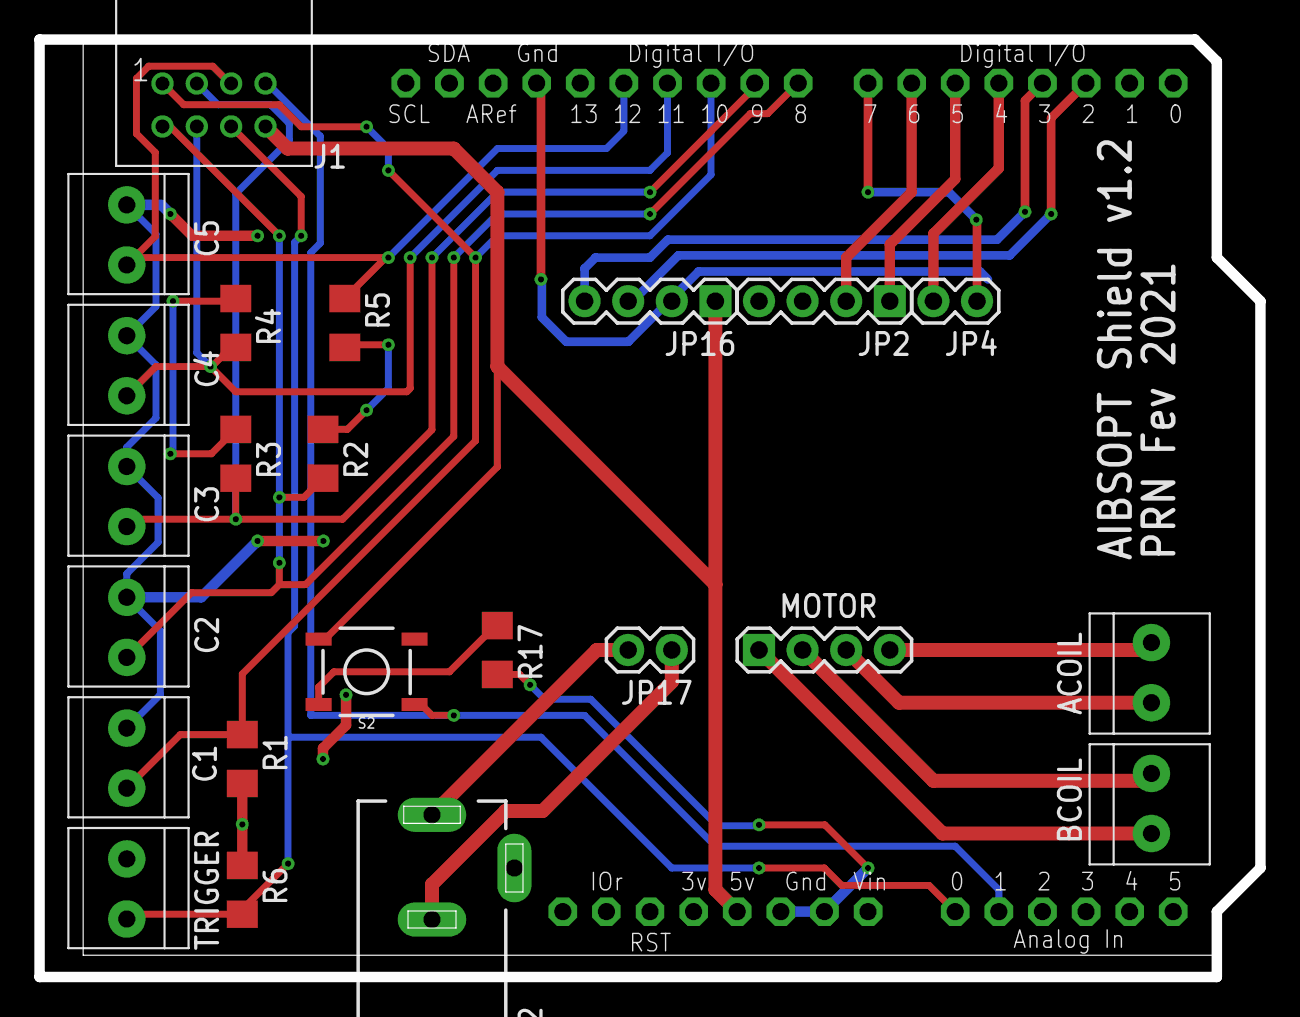
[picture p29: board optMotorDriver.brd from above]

Board: 2 copper layers, 71.1 x 54.6 mm, 24 parts (0 on the bottom side), 22 nets.

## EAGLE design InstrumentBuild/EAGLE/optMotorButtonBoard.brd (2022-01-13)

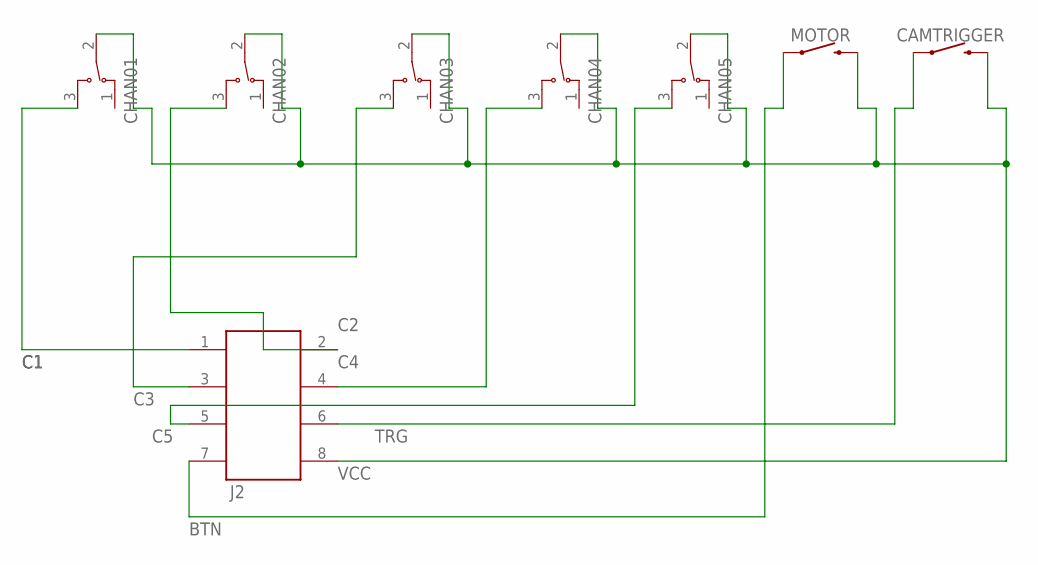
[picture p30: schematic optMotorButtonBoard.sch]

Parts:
CAMTRIGGER: MOMENTARY-SWITCH-SPST-PTH-12MM; TACTILE_SWITCH_PTH_12MM
CHAN01, CHAN02, CHAN03, CHAN04, CHAN05: ATE1E-2M3-10-Z
J2: 62400821722
MOTOR: MOMENTARY-SWITCH-SPST-PTH-12MM; TACTILE_SWITCH_PTH_12MM

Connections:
BTN: J2.7 (1), MOTOR.1
C1: CHAN01.3, J2.1 (7)
C2: CHAN02.3, J2.2 (8)
C3: CHAN03.3, J2.3 (5)
C4: CHAN04.3, J2.4 (6)
C5: CHAN05.3, J2.5 (3)
TRG: CAMTRIGGER.1, J2.6 (4)
VCC: CAMTRIGGER.3 (2), CHAN01.2, CHAN02.2, CHAN03.2, CHAN04.2, CHAN05.2, J2.8 (2), MOTOR.3 (2)

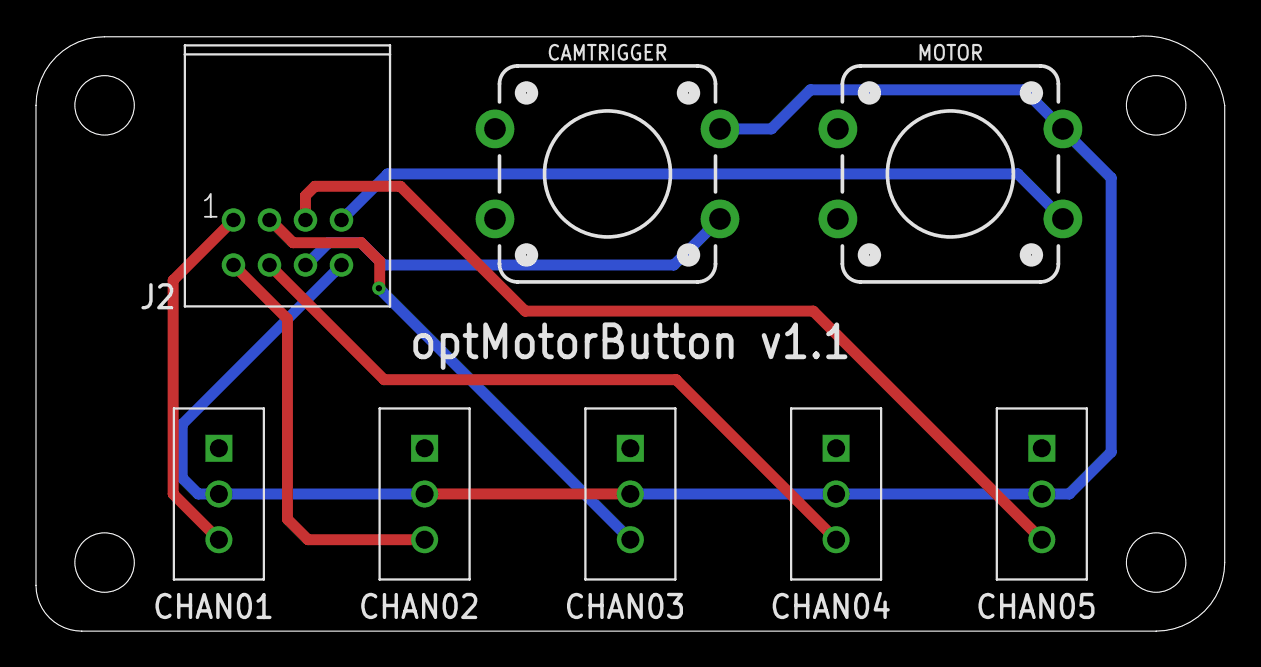
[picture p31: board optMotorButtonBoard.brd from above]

Board: 2 copper layers, 66.0 x 33.1 mm, 12 parts (0 on the bottom side), 8 nets.

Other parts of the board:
U$1, U$2, U$3, U$4: STAND-OFF

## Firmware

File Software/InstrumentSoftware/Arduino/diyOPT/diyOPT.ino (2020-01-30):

/****************************************************************************** 
AIBSopt optDriverBoard shield sketch.
Drives stepper motor with BigEasyDriver.
Toggles pins for illumination through channels 1-5. 

Motor driver code based on:

SparkFun Big Easy Driver Basic Demo
Toni Klopfenstein @ SparkFun Electronics
February 2015
https://github.com/sparkfun/Big_Easy_Driver

PRNicovich
Allen Institute for Brain Science
2019

******************************************************************************/
//Declare pin functions on Arduino
#define stp 2
#define dir 3
#define MS1 4
#define MS2 5
#define MS3 6
#define EN  7
#define btn 15
#define led 13
#define chan1 10
#define chan2 8
#define chan3 9
#define chan4 11
#define chan5 12

//Declare variables for functions
char user_input;
int x;
int y;
int state;

int buttonState;             // the current reading from the input pin
int lastButtonState = LOW;
unsigned long lastDebounceTime = 0;  // the last time the output pin was toggled
unsigned long debounceDelay = 50;    // the debounce time; increase if the output flickers

void setup() {
  pinMode(stp, OUTPUT);
  pinMode(dir, OUTPUT);
  pinMode(MS1, OUTPUT);
  pinMode(MS2, OUTPUT);
  pinMode(MS3, OUTPUT);
  pinMode(EN, OUTPUT);
  pinMode(btn, INPUT);
  pinMode(led, OUTPUT);
  pinMode(chan1, OUTPUT);
  pinMode(chan2, OUTPUT);
  pinMode(chan3, OUTPUT);
  pinMode(chan4, OUTPUT);
  pinMode(chan5, OUTPUT);

  digitalWrite(EN, LOW); //Pull enable pin low to set FETs active and allow motor control

  digitalWrite(chan1, LOW);
  digitalWrite(chan2, LOW);
  digitalWrite(chan3, LOW);
  digitalWrite(chan4, LOW);
  digitalWrite(chan5, LOW);
  
  resetBEDPins(); //Set step, direction, microstep and enable pins to default states
  
  Serial.begin(9600); //Open Serial connection for debugging
  Serial.println("Begin motor control");
  Serial.println();
  //Print function list for user selection
  Serial.println("Enter number for control option:");
  Serial.println("1. Turn at default microstep mode.");
  Serial.println("2. Reverse direction at default microstep mode.");
  Serial.println("3. Turn at 1/16th microstep mode.");
  Serial.println("4. Step forward and reverse directions.");
  Serial.println("5. Step default step forward.");
  Serial.println("6. Step default step reverse.");
  Serial.println("7. Step micro step forward.");
  Serial.println("8. Step micro step reverse.");
  Serial.println("9. Step 16 x 1/16th microsteps forward.");
  Serial.println("A. Step 16 x 1/16th microsteps reverse.");
  Serial.println();
}

//Main loop
void loop() {
  while(Serial.available()){
      user_input = Serial.read(); //Read user input and trigger appropriate function
      
      if (user_input =='1')
      {
         StepForwardDefault();
      }
      else if(user_input =='2')
      {
        ReverseStepDefault();
      }
      else if(user_input =='3')
      {
        SmallStepMode();
      }
      else if(user_input =='4')
      {
        ForwardBackwardStep();
      }
      else if(user_input =='5')
      {
        ForwardSingleStepDefault();
      }
      else if(user_input =='6')
      {
        ReverseSingleStepDefault();
      }
      else if(user_input =='7')
      {
        ForwardSingleStepMicrostep();
      }
      else if(user_input =='8')
      {
        ReverseSingleStepMicrostep();
      }
      else if(user_input =='9')
      {
        SixteenMicrostepsForward();
      }
      else if(user_input =='A')
      {
        SixteenMicrostepsForward();
      }
      else if(user_input == 'T')
      {
        digitalWrite(chan1, HIGH);
      }
      else if(user_input == 't')
      {
        digitalWrite(chan1, LOW);
      }
      else if(user_input == 'F')
      {
        digitalWrite(chan2, HIGH);
      }
      else if(user_input == 'f')
      {
        digitalWrite(chan2, LOW);
      }
      else if(user_input == 'G')
      {
        digitalWrite(chan3, HIGH);
      }
      else if(user_input == 'g')
      {
        digitalWrite(chan3, LOW);
      }
      else if(user_input == 'H')
      {
        digitalWrite(chan4, HIGH);
      }
      else if(user_input == 'h')
      {
        digitalWrite(chan4, LOW);
      }
      else if(user_input == 'J')
      {
        digitalWrite(chan5, HIGH);
      }
      else if(user_input == 'j')
      {
        digitalWrite(chan5, LOW);
      }

      else if (user_input == '\n'){
        // if newline char do nothing
      }
      
      else
      {
        Serial.println("Invalid option entered.");
      } 
      } // serial available


      int reading = digitalRead(btn);
      if (reading != lastButtonState) {

          // State change here
          lastDebounceTime = millis();
          
          //Serial.println("bounce");
          
          }

      if ((millis() - lastDebounceTime) > debounceDelay) {

          if (reading == HIGH) {
            
            ledToggle(reading);
            
            ReverseSingleStepDefault();
          }
          else if (reading == LOW) {
            ledToggle(reading);
          }
          
      }   

      lastButtonState = reading;
      
      
  }

void ledToggle(bool state){
  digitalWrite(led, state);
}


//Reset Big Easy Driver pins to default states
void resetBEDPins()
{
  digitalWrite(stp, LOW);
  digitalWrite(dir, LOW);
  digitalWrite(MS1, LOW);
  digitalWrite(MS2, LOW);
  digitalWrite(MS3, LOW);
 // digitalWrite(EN, HIGH);
}

//Default microstep mode function
void StepForwardDefault()
{
  Serial.println("Moving forward at default step mode.");
  digitalWrite(dir, LOW); //Pull direction pin low to move "forward"
  for(x= 1; x<1000; x++)  //Loop the forward stepping enough times for motion to be visible
  {
    digitalWrite(stp,HIGH); //Trigger one step forward
    delay(1);
    digitalWrite(stp,LOW); //Pull step pin low so it can be triggered again
    delay(1);
  }
  resetBEDPins();
  Serial.println("Enter new option");
  Serial.println();
}

//Reverse default microstep mode function
void ReverseStepDefault()
{
  Serial.println("Moving in reverse at default step mode.");
  digitalWrite(dir, HIGH); //Pull direction pin high to move in "reverse"
  for(x= 1; x<1000; x++)  //Loop the stepping enough times for motion to be visible
  {
    digitalWrite(stp,HIGH); //Trigger one step
    delay(1);
    digitalWrite(stp,LOW); //Pull step pin low so it can be triggered again
    delay(1);
  }
  resetBEDPins();
  Serial.println("Enter new option");
  Serial.println();
}

// 1/16th microstep foward mode function
void SmallStepMode()
{
  Serial.println("Stepping at 1/16th microstep mode.");
  digitalWrite(dir, LOW); //Pull direction pin low to move "forward"
  digitalWrite(MS1, HIGH); //Pull MS1,MS2, and MS3 high to set logic to 1/16th microstep resolution
  digitalWrite(MS2, HIGH);
  digitalWrite(MS3, HIGH);
  for(x= 1; x<1000; x++)  //Loop the forward stepping enough times for motion to be visible
  {
    digitalWrite(stp,HIGH); //Trigger one step forward
    delay(1);
    digitalWrite(stp,LOW); //Pull step pin low so it can be triggered again
    delay(1);
  }
  resetBEDPins();
  Serial.println("Enter new option");
  Serial.println();
}

//Forward/reverse stepping function
void ForwardBackwardStep()
{
  Serial.println("Alternate between stepping forward and reverse.");
  for(x= 1; x<5; x++)  //Loop the forward stepping enough times for motion to be visible
  {
    //Read direction pin state and change it
    state=digitalRead(dir);
    if(state == HIGH)
    {
      digitalWrite(dir, LOW);
    }
    else if(state ==LOW)
    {
      digitalWrite(dir,HIGH);
    }
    
    for(y=1; y<1000; y++)
    {
      digitalWrite(stp,HIGH); //Trigger one step
      delay(1);
      digitalWrite(stp,LOW); //Pull step pin low so it can be triggered again
      delay(1);
    }
  }
  resetBEDPins();
  Serial.println("Enter new option");
  Serial.println();
}

//One standard step forward
void ForwardSingleStepDefault()
{
  Serial.println("step");
  //Serial.println("Moving forward at default step mode.");
  digitalWrite(dir, LOW); //Pull direction pin low to move "forward"
  for(x= 1; x<2; x++)  //Loop the forward stepping enough times for motion to be visible
  {
    digitalWrite(stp,HIGH); //Trigger one step forward
    delay(1);
    digitalWrite(stp,LOW); //Pull step pin low so it can be triggered again
    delay(1);
  }
  resetBEDPins();
  //Serial.println("Enter new option");
  Serial.println();
}

//Reverse default microstep mode function
void ReverseSingleStepDefault()
{
 // Serial.println("Moving in reverse at default step mode.");
  digitalWrite(dir, HIGH); //Pull direction pin high to move in "reverse"
  for(x= 1; x<2; x++)  //Loop the stepping enough times for motion to be visible
  {
    digitalWrite(stp,HIGH); //Trigger one step
    delay(1);
    digitalWrite(stp,LOW); //Pull step pin low so it can be triggered again
    delay(1);
  }
  resetBEDPins();
  //Serial.println("Enter new option");
  Serial.println();
}

//One 1/16th microstep step forward
void ForwardSingleStepMicrostep()
{
 // Serial.println("Moving forward at default step mode.");
  digitalWrite(dir, LOW); //Pull direction pin low to move "forward"
  digitalWrite(MS1, HIGH); //Pull MS1,MS2, and MS3 high to set logic to 1/16th microstep resolution
  digitalWrite(MS2, HIGH);
  digitalWrite(MS3, HIGH);
  for(x= 1; x<2; x++)  //Loop the forward stepping enough times for motion to be visible
  {
    digitalWrite(stp,HIGH); //Trigger one step forward
    delay(1);
    digitalWrite(stp,LOW); //Pull step pin low so it can be triggered again
    delay(1);
  }
  resetBEDPins();
  //Serial.println("Enter new option");
  Serial.println();
}

//Reverse 1/16th microstep mode single step
void ReverseSingleStepMicrostep()
{
 // Serial.println("Moving in reverse at default step mode.");
  digitalWrite(dir, HIGH); //Pull direction pin high to move in "reverse"
  digitalWrite(MS1, HIGH); //Pull MS1,MS2, and MS3 high to set logic to 1/16th microstep resolution
  digitalWrite(MS2, HIGH);
  digitalWrite(MS3, HIGH);
  for(x= 1; x<2; x++)  //Loop the stepping enough times for motion to be visible
  {
    digitalWrite(stp,HIGH); //Trigger one step
    delay(1);
    digitalWrite(stp,LOW); //Pull step pin low so it can be triggered again
    delay(1);
  }
  resetBEDPins();
  //Serial.println("Enter new option");
  Serial.println();
}

//Sixteen 1/16th microsteps step forward
void SixteenMicrostepsForward()
{
 // Serial.println("Moving forward at default step mode.");
  digitalWrite(dir, LOW); //Pull direction pin low to move "forward"
  digitalWrite(MS1, HIGH); //Pull MS1,MS2, and MS3 high to set logic to 1/16th microstep resolution
  digitalWrite(MS2, HIGH);
  digitalWrite(MS3, HIGH);
  for(x= 0; x<16; x++)  //Loop the forward stepping enough times for motion to be visible
  {
    digitalWrite(stp,HIGH); //Trigger one step forward
    delay(1);
    digitalWrite(stp,LOW); //Pull step pin low so it can be triggered again
    delay(1);
  }
  resetBEDPins();
  //Serial.println("Enter new option");
  Serial.println();
}

//Sixteen 1/16th microsteps step reverse
void SixteenMicrostepsReverse()
{
 // Serial.println("Moving forward at default step mode.");
  digitalWrite(dir, HIGH); //Pull direction pin low to move "forward"
  digitalWrite(MS1, HIGH); //Pull MS1,MS2, and MS3 high to set logic to 1/16th microstep resolution
  digitalWrite(MS2, HIGH);
  digitalWrite(MS3, HIGH);
  for(x= 0; x<16; x++)  //Loop the forward stepping enough times for motion to be visible
  {
    digitalWrite(stp,HIGH); //Trigger one step forward
    delay(1);
    digitalWrite(stp,LOW); //Pull step pin low so it can be triggered again
    delay(1);
  }
  resetBEDPins();
  //Serial.println("Enter new option");
  Serial.println();
}

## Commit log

2019-09-28 Initial commit to repo.
    [ACL2520U-DG6-A-Solidworks.sldprt, BE1-Solidworks.sldprt, BE1R-Solidworks.sldprt, BearingShaft.step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]
2019-10-14 Create README.md
    Added readme for CAD and assembly parts.
2019-10-15 Reorg and clean-up prior to release. Removed excess CAD files from commercial makers. Added software for alignment and post-processing of images as acquired by MicroManager files. Renamed folders to 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
    [ACL2520U-DG6-A-Solidworks.sldprt, BE1-Solidworks.sldprt, BE1R-Solidworks.sldprt, BearingShaft.step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]
2019-10-15 Added example gif. Removed incorrect schematic file.
    [BigEasyDriver_v16a.brd, BigEasyDriver_v16a.sch, optMotorDriver.sch]
2020-01-30 Updated diyOPT.ino file to reflect changes for motor driver PCB.
2020-01-30 Update schematics and readme for driver board.
    [PartsList20181210.xlsx, optMotorDriver.sch]
2020-01-30 Add files for driver board, button board, and BOM.
    [optMotorButtonBoard.brd, optMotorButtonBoard.sch, optMotorDriver.brd]
2020-01-30 Added files for mount for optButtonBoard
    [OPTButtonBoardTableMount.dxf]
2020-01-30 Update readme files to include motor driver PCB information
2020-01-30 Update header of Arduino sketch.
2020-03-10 Replace license, contribution agreement files with .docx files. Add laserLaunch folders and files. Add CAD files and update specimenChamberBuildNotes.txt to support commercial cuvette.
    [CuvetteStandAssembly.step, HexLightPipeToSM1Adapter.step, HexLightPipeToSM1Adapter.stl, OPTCuvetteBase.step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]
2020-03-10 Added sheet for laserLaunch in ./InstrumentBuild/PartsList20181210.xlsx. Sheet contains no data.
    [PartsList20181210.xlsx]
2020-05-14 Update optMotorDriver BOM.txt
    Correct links to PCBs
2021-02-20 Updated top silk and added board's name to top.
    [optMotorButtonBoard.brd, optMotorButtonBoard.sch]
2021-02-20 Updated top silk, removed some layout corners and increased version to 1.2.
    [optMotorDriver.brd, optMotorDriver.sch]

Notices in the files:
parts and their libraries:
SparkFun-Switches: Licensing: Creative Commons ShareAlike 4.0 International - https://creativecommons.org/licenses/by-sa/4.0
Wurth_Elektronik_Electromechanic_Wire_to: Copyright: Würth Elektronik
